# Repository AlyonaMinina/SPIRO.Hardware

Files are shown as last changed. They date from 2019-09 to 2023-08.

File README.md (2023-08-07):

<p align="center">
  SPIRO
</p>
<p align="center">
    <b>S</b>mart <b>P</b>late <b>I</b>maging <b>Ro</b>bot
</p>

[SPIRO](https://www.alyonaminina.org/spiro) is a smart robot for automated time-lapse imaging of biological samples grown on vertically positioned Petri plates: plant seeds, seedlings, bacterial colonies, fungal mycelia, moss etc. The preprint version of our manuscript is available [here](https://www.biorxiv.org/content/10.1101/2021.03.15.435343v1).

SPIRO is controlled by designated software and operated remotely using a web-based user interface [(GitHub repo)](https://github.com/jonasoh/spiro).

We developed two assays to analyze data produced by SPIRO: germination tracking assay optimized for *Arabidopsis thaliana* seeds and root growth tracking assay optimized for *Arabidopsis thaliana* seedlings [(GitHub repo)](https://github.com/jiaxuanleong/spiro-IJmacros).

The SPIRO hardware is constructed from eleven sets of 3D printable structural parts. Sets 3a and 3b are for alternative setups that include either the Arducam motorized focus camera module or the Raspberry Pi v2 camera with manual focus, respectively. Step by step instructions for printing and assembling SPIRO are provided in [the assembly instructions](https://github.com/AlyonaMinina/SPIRO.Hardware/raw/master/1.%20Assembly%20Instructions/SPIRO%20assembly%20instructions.pdf). 

Please refer to **[Table S1](https://github.com/AlyonaMinina/SPIRO.Hardware/raw/master/2.%20Supplementary%20Tables/Table%20S1.%20List%20of%20components%20to%20be%20purchased.pdf)** for the list of components to be purchased and to **[Table S2](https://github.com/AlyonaMinina/SPIRO.Hardware/blob/master/2.%20Supplementary%20Tables/Table%20S2.%20Structural%20parts%20of%20SPIRO%20for%203D%20printing.md)** for instructions on 3D printing. Table S2 also contains several useful accessories for improving the usability of SPIRO.

<p align="center">
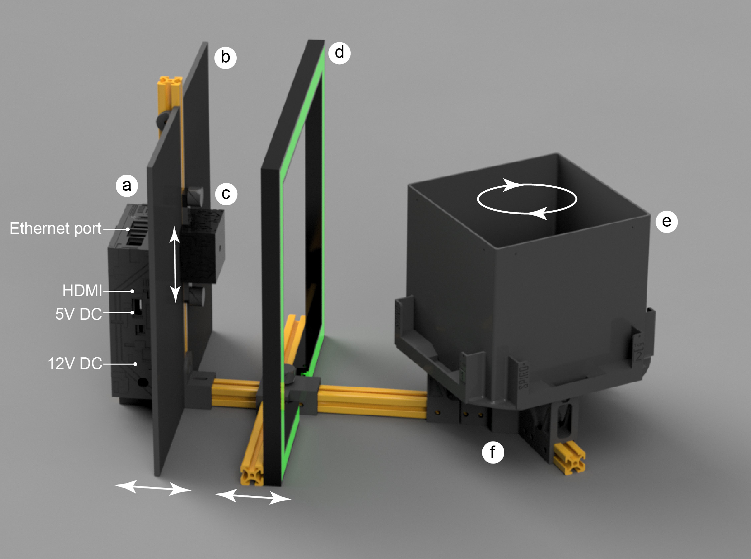
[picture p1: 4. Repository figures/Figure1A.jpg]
SPIRO
  
  SPIRO
</p>

**Figure 1**. SPIRO structure: **a**, Borg's nest harboring the electronics; **b**, vertical rail with the light screen, both can slide along the horizontal rail; **c**, camera house, with adjustable position on the vertical; **d**, LED frame with diffusors, position along the horizontal rail can be adjusted; **e**, rotating stage to hold Petri plates; **f**, motor hub harboring the stepper motor and connecting the horizontal rails. 

<p align="center">
  <br />This work is licensed under a <a rel="license" href="http://creativecommons.org/licenses/by/4.0/">Creative Commons Attribution 4.0 International License</a>.
 </p>

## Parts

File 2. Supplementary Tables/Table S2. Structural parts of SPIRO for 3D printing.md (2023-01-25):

# Table S2. SPIRO components for 3D printing

# Structural parts

| STL file                                                     | Rotation        | Supports    | Brim | Infill | Filament    | Additional info                                              |
| ------------------------------------------------------------ | --------------- | ----------- | ---- | ------ | ----------- | ------------------------------------------------------------ |
| [Set 1](https://github.com/AlyonaMinina/SPIRO.Hardware/raw/master/3.%20Files%20for%20SPIRO%203D%20printable%20hardware/SPIRO%20hardware%20component%20sets/stl%20files/Set%2001.%20Alyona%20Minina.%202019.%20UHEI.stl)| X: 90°          | Build plate | No   | 20%    | Matte black | <details><summary>Set 1. upgraded 2021.05.18 </summary><br/>  [.3mf project file](https://github.com/AlyonaMinina/SPIRO.Hardware/raw/master/3.%20Files%20for%20SPIRO%203D%20printable%20hardware/SPIRO%20hardware%20component%20sets/3mf%20files/Set%2001.%20Alyona%20Minina.%202019.%20UHEI.3mf) <br/>   [.f3d Autodesk Fusion 360 file](https://github.com/AlyonaMinina/SPIRO.Hardware/raw/master/3.%20Files%20for%20SPIRO%203D%20printable%20hardware/SPIRO%20hardware%20component%20sets/Autodesk%20Fusion%20360%20files/Set%2001.%20Alyona%20Minina.%202019.%20UHEI.f3d) <br/> [Preview of layout in Slic3r](https://raw.githubusercontent.com/AlyonaMinina/SPIRO.Hardware/master/3.%20Files%20for%20SPIRO%203D%20printable%20hardware/SPIRO%20hardware%20component%20sets/Screenshots%20of%20slic3r/set%2001.jpg) <br/><br/>**Components list:** <br/>1.	 Motor hub v2 (smoothened corners) <br/>2.	 2x bearing guides<br/>3.	 1x bearing guide with the mount for the mini microswitch v2 (stabilizing the switch)<br/>4. Mini microswitch housing v2  (stabilizing the switch)<br/>5. Mini microswitch pin (tiny dick)<br/>6. Holder for the vertical rail<br/>7. Holder for the LED frame rail<br/>8. 2x bottom for a thumb screw<br/>9. 2x cap for a thumb screw<br/><br/>**Filament use**: 135 g <br/><br/>**Printing time:** 13 h</details> |
| [Set 2](https://github.com/AlyonaMinina/SPIRO.Hardware/raw/master/3.%20Files%20for%20SPIRO%203D%20printable%20hardware/SPIRO%20hardware%20component%20sets/stl%20files/Set%2002.%20Alyona%20Minina.%202019.%20UHEI.stl) | –               | Build plate | No   | 20%    | Matte black | <details><summary>Set 2. upgraded 2021.05.20</summary><br/> [.3mf project file](https://github.com/AlyonaMinina/SPIRO.Hardware/raw/master/3.%20Files%20for%20SPIRO%203D%20printable%20hardware/SPIRO%20hardware%20component%20sets/3mf%20files/Set%2002.%20Alyona%20Minina.%202019.%20UHEI.3mf) <br/> [.f3d Autodesk Fusion 360 file](https://github.com/AlyonaMinina/SPIRO.Hardware/raw/master/3.%20Files%20for%20SPIRO%203D%20printable%20hardware/SPIRO%20hardware%20component%20sets/Autodesk%20Fusion%20360%20files/Set%2002.%20Alyona%20Minina.%202019.%20UHEI.f3d) <br/> [Preview of layout in Slic3r](https://raw.githubusercontent.com/AlyonaMinina/SPIRO.Hardware/master/3.%20Files%20for%20SPIRO%203D%20printable%20hardware/SPIRO%20hardware%20component%20sets/Screenshots%20of%20slic3r/set%2002.jpg)<br/><br/>**Components list:** <br/>1.	Borg's nest (adjusted ethernet port)<br/>2. Lid for the Borg's nest<br/>3. Lid for the DC connector<br/>4. Holder for the SparkFun MOSFET power control kit<br/><br/>**PLA use**: 210 g <br/><br/>**Printing time:** 18.5 h<br/></details> |
| [Set 3a](https://github.com/AlyonaMinina/SPIRO.Hardware/raw/master/3.%20Files%20for%20SPIRO%203D%20printable%20hardware/SPIRO%20hardware%20component%20sets/stl%20files/Set%2003a.%20Alyona%20Minina.%202019.%20UHEI.stl) | X: 90°          | Build plate | No   | 20%    | Matte black | <details><summary>Set 3a</summary><br/>[.3mf project file](https://github.com/AlyonaMinina/SPIRO.Hardware/raw/master/3.%20Files%20for%20SPIRO%203D%20printable%20hardware/SPIRO%20hardware%20component%20sets/3mf%20files/Set%2003a.%20Alyona%20Minina.%202019.%20UHEI.3mf)<br/> [.f3d Autodesk Fusion 360 file](https://github.com/AlyonaMinina/SPIRO.Hardware/raw/master/3.%20Files%20for%20SPIRO%203D%20printable%20hardware/SPIRO%20hardware%20component%20sets/Autodesk%20Fusion%20360%20files/Set%2003a.%20Alyona%20Minina.%202019.%20UHEI.f3d)<br/> [Preview of layout in Slic3r](https://raw.githubusercontent.com/AlyonaMinina/SPIRO.Hardware/master/3.%20Files%20for%20SPIRO%203D%20printable%20hardware/SPIRO%20hardware%20component%20sets/Screenshots%20of%20slic3r/set%2003a.PNG)<br/><br/>**Components list:** <br/>1. Camera housing for Arducam module<br/>2. Lid for the camera housing<br/>3. 2x cap for a thumb screw<br/>4. 2x bottom for a thumb screw<br/>5. washers<br/><br/>**PLA use**: 50 g <br/><br/>**Printing time:** 5 h<br/></details> |
| [Set 3b](https://github.com/AlyonaMinina/SPIRO.Hardware/raw/master/3.%20Files%20for%20SPIRO%203D%20printable%20hardware/SPIRO%20hardware%20component%20sets/stl%20files/Set%2003b.%20Alyona%20Minina.%202019.%20UHEI.stl) | X: 90°          | Build plate | No   | 20%    | Matte black | <details><summary>Set 3b</summary><br/>[.3mf project file](https://github.com/AlyonaMinina/SPIRO.Hardware/raw/master/3.%20Files%20for%20SPIRO%203D%20printable%20hardware/SPIRO%20hardware%20component%20sets/3mf%20files/Set%2003b.%20Alyona%20Minina.%202019.%20UHEI.3mf) <br/> [.f3d Autodesk Fusion 360 file](https://github.com/AlyonaMinina/SPIRO.Hardware/raw/master/3.%20Files%20for%20SPIRO%203D%20printable%20hardware/SPIRO%20hardware%20component%20sets/Autodesk%20Fusion%20360%20files/Set%2003b.%20Alyona%20Minina.%202019.%20UHEI.f3d)<br/> [Preview of layout in Slic3r](https://raw.githubusercontent.com/AlyonaMinina/SPIRO.Hardware/master/3.%20Files%20for%20SPIRO%203D%20printable%20hardware/SPIRO%20hardware%20component%20sets/Screenshots%20of%20slic3r/set%2003b.PNG)<br/><br/>**Components list:** <br/>1. Camera housing for RPi camera<br/>2. Lid for the camera housing<br/>3. 2x bottom for a thumb screw<br/>4. 2x cap for a thumb screw<br/>5. Focusing tool<br/>6. Stabilizer for the camera <br/><br/>**PLA use**: 25 g <br/><br/>**Printing time:** 3 h<br/></details> |
| [Set 4](https://github.com/AlyonaMinina/SPIRO.Hardware/raw/master/3.%20Files%20for%20SPIRO%203D%20printable%20hardware/SPIRO%20hardware%20component%20sets/stl%20files/Set%2004.%20Alyona%20Minina.%202019.%20UHEI.stl) | X: 270°         | Build plate | No   | 20%    | Matte black | <details><summary>Set 4. upgraded 2021.05.20</summary><br/>[.3mf project file](https://github.com/AlyonaMinina/SPIRO.Hardware/raw/master/3.%20Files%20for%20SPIRO%203D%20printable%20hardware/SPIRO%20hardware%20component%20sets/3mf%20files/Set%2004.%20Alyona%20Minina.%202019.%20UHEI.3mf) <br/> [.f3d Autodesk Fusion 360 file](https://github.com/AlyonaMinina/SPIRO.Hardware/raw/master/3.%20Files%20for%20SPIRO%203D%20printable%20hardware/SPIRO%20hardware%20component%20sets/Autodesk%20Fusion%20360%20files/Set%2004.%20Alyona%20Minina.%202019.%20UHEI.f3d) <br/> [Preview of layout in Slic3r](https://raw.githubusercontent.com/AlyonaMinina/SPIRO.Hardware/master/3.%20Files%20for%20SPIRO%203D%20printable%20hardware/SPIRO%20hardware%20component%20sets/Screenshots%20of%20slic3r/set%2004.jpg)<br/><br/>**Components list:** <br/>1. Cube. The rotating stage with holders for Petri plates (adjusted tiny dick orientation) <br/><br/>**PLA use**: 380 g <br/><br/>**Printing time:** 28.5 h<br/></details> |
| [Set 5](https://github.com/AlyonaMinina/SPIRO.Hardware/raw/master/3.%20Files%20for%20SPIRO%203D%20printable%20hardware/SPIRO%20hardware%20component%20sets/stl%20files/Set%2005.%20Alyona%20Minina.%202019.%20UHEI.stl) | Z: 345°  | Everywhere  | Yes  | 50%    | Matte black | <details><summary>Set 5</summary><br/>[.3mf project file](https://github.com/AlyonaMinina/SPIRO.Hardware/raw/master/3.%20Files%20for%20SPIRO%203D%20printable%20hardware/SPIRO%20hardware%20component%20sets/3mf%20files/Set%2005.%20Alyona%20Minina.%202019.%20UHEI.3mf) <br/> [.f3d Autodesk Fusion 360 file](https://github.com/AlyonaMinina/SPIRO.Hardware/raw/master/3.%20Files%20for%20SPIRO%203D%20printable%20hardware/SPIRO%20hardware%20component%20sets/Autodesk%20Fusion%20360%20files/Set%2005.%20Alyona%20Minina.%202019.%20UHEI.f3d) <br/> [Preview of layout in Slic3r](https://raw.githubusercontent.com/AlyonaMinina/SPIRO.Hardware/master/3.%20Files%20for%20SPIRO%203D%20printable%20hardware/SPIRO%20hardware%20component%20sets/Screenshots%20of%20slic3r/set%2005.jpg)<br/><br/>**Components list:** <br/>1. The right half of the light screen<br/><br/>**PLA use**: 260 g <br/><br/>**Printing time:** 23 h<br/><br/>**Notes:** Please ignore messages about toolpath being detected outside the perimeter.</details> |
| [Set 6](https://github.com/AlyonaMinina/SPIRO.Hardware/raw/master/3.%20Files%20for%20SPIRO%203D%20printable%20hardware/SPIRO%20hardware%20component%20sets/stl%20files/Set%2006.%20Alyona%20Minina.%202019.%20UHEI.stl) |  Z: 355° | Everywhere  | Yes  | 50%    | Matte black | <details><summary>Set 6</summary><br/>[.3mf project file](https://github.com/AlyonaMinina/SPIRO.Hardware/raw/master/3.%20Files%20for%20SPIRO%203D%20printable%20hardware/SPIRO%20hardware%20component%20sets/3mf%20files/Set%2006.%20Alyona%20Minina.%202019.%20UHEI.3mf) <br/> [.f3d Autodesk Fusion 360 file](https://github.com/AlyonaMinina/SPIRO.Hardware/raw/master/3.%20Files%20for%20SPIRO%203D%20printable%20hardware/SPIRO%20hardware%20component%20sets/Autodesk%20Fusion%20360%20files/Set%2006.%20Alyona%20Minina.%202019.%20UHEI.f3d)<br/> [Preview of layout in Slic3r](https://raw.githubusercontent.com/AlyonaMinina/SPIRO.Hardware/master/3.%20Files%20for%20SPIRO%203D%20printable%20hardware/SPIRO%20hardware%20component%20sets/Screenshots%20of%20slic3r/set%2006.jpg)<br/><br/>**Components list:** <br/>1. The left half of the light screen<br/><br/>**PLA use**: 230 g <br/><br/>**Printing time:** 20.5 h<br/><br/>**Notes:** Please ignore messages about toolpath being detected outside the perimeter.</details> |
| [Set 7](https://github.com/AlyonaMinina/SPIRO.Hardware/raw/master/3.%20Files%20for%20SPIRO%203D%20printable%20hardware/SPIRO%20hardware%20component%20sets/stl%20files/Set%2007.%20Alyona%20Minina.%202019.%20UHEI.stl) | Z: 50°          | Everywhere  | Yes  | 20%   | Matte black | <details><summary>Set 7</summary><br/>[.3mf project file](https://github.com/AlyonaMinina/SPIRO.Hardware/raw/master/3.%20Files%20for%20SPIRO%203D%20printable%20hardware/SPIRO%20hardware%20component%20sets/3mf%20files/Set%2007.%20Alyona%20Minina.%202019.%20UHEI.3mf) <br/> [.f3d Autodesk Fusion 360 file](https://github.com/AlyonaMinina/SPIRO.Hardware/raw/master/3.%20Files%20for%20SPIRO%203D%20printable%20hardware/SPIRO%20hardware%20component%20sets/Autodesk%20Fusion%20360%20files/Set%2007.%20Alyona%20Minina.%202019.%20UHEI.f3d) <br/> [Preview of layout in Slic3r](https://raw.githubusercontent.com/AlyonaMinina/SPIRO.Hardware/master/3.%20Files%20for%20SPIRO%203D%20printable%20hardware/SPIRO%20hardware%20component%20sets/Screenshots%20of%20slic3r/set%2007.jpg)<br/><br/>**Components list:** <br/>1. The right half of the LED frame<br/><br/>**PLA use**: 140 g <br/><br/>**Printing time:** 14 h<br/><br/>**Notes:** Please ignore messages about toolpath being detected outside the perimeter.</details> |
| [Set 8](https://github.com/AlyonaMinina/SPIRO.Hardware/raw/master/3.%20Files%20for%20SPIRO%203D%20printable%20hardware/SPIRO%20hardware%20component%20sets/stl%20files/Set%2008.%20Alyona%20Minina.%202019.%20UHEI.stl) | Z: 50°          | Everywhere  | Yes  | 20%    | Matte black | <details><summary>Set 8</summary><br/>[.3mf project file](https://github.com/AlyonaMinina/SPIRO.Hardware/raw/master/3.%20Files%20for%20SPIRO%203D%20printable%20hardware/SPIRO%20hardware%20component%20sets/3mf%20files/Set%2008.%20Alyona%20Minina.%202019.%20UHEI.3mf) <br/> [.f3d Autodesk Fusion 360 file](https://github.com/AlyonaMinina/SPIRO.Hardware/raw/master/3.%20Files%20for%20SPIRO%203D%20printable%20hardware/SPIRO%20hardware%20component%20sets/Autodesk%20Fusion%20360%20files/Set%2008.%20Alyona%20Minina.%202019.%20UHEI.f3d)<br/> [Preview of layout in Slic3r](https://raw.githubusercontent.com/AlyonaMinina/SPIRO.Hardware/master/3.%20Files%20for%20SPIRO%203D%20printable%20hardware/SPIRO%20hardware%20component%20sets/Screenshots%20of%20slic3r/set%2008.jpg)<br/><br/>**Components list:** <br/>1. The left half of the LED frame<br/><br/>**PLA use**: 130 g <br/><br/>**Printing time:** 12.5 h<br/><br/>**Notes:** Please ignore messages about toolpath being detected outside the perimeter.</details> |
| [Set 9](https://github.com/AlyonaMinina/SPIRO.Hardware/raw/master/3.%20Files%20for%20SPIRO%203D%20printable%20hardware/SPIRO%20hardware%20component%20sets/stl%20files/Set%2009.%20Alyona%20Minina.%202019.%20UHEI.stl) | Z: 50°          | –           | Yes  | 30%    | Transparent | <details><summary>Set 9</summary><br/>[.3mf project file](https://github.com/AlyonaMinina/SPIRO.Hardware/raw/master/3.%20Files%20for%20SPIRO%203D%20printable%20hardware/SPIRO%20hardware%20component%20sets/3mf%20files/Set%2009.%20Alyona%20Minina.%202019.%20UHEI.3mf) <br/> [.f3d Autodesk Fusion 360 file](https://github.com/AlyonaMinina/SPIRO.Hardware/raw/master/3.%20Files%20for%20SPIRO%203D%20printable%20hardware/SPIRO%20hardware%20component%20sets/Autodesk%20Fusion%20360%20files/Set%2009.%20Alyona%20Minina.%202019.%20UHEI.f3d) <br/> [Preview of layout in Slic3r](https://raw.githubusercontent.com/AlyonaMinina/SPIRO.Hardware/master/3.%20Files%20for%20SPIRO%203D%20printable%20hardware/SPIRO%20hardware%20component%20sets/Screenshots%20of%20slic3r/set%2009.jpg) <br/><br/>**Components list:** <br/>1. Left diffuser<br/>2. Bottom left diffuser<br/>3. Bottom right diffuser<br/><br/>**PLA use**: 35 g <br/><br/>**Printing time:** 2.5 h<br/></details> |
| [Set 10](https://github.com/AlyonaMinina/SPIRO.Hardware/raw/master/3.%20Files%20for%20SPIRO%203D%20printable%20hardware/SPIRO%20hardware%20component%20sets/stl%20files/Set%2010.%20Alyona%20Minina.%202019.%20UHEI.stl) | Z: 40°          | –           | Yes  | 30%    | Transparent | <details><summary>Set 10</summary><br/>[.3mf project file](https://github.com/AlyonaMinina/SPIRO.Hardware/raw/master/3.%20Files%20for%20SPIRO%203D%20printable%20hardware/SPIRO%20hardware%20component%20sets/3mf%20files/Set%2010.%20Alyona%20Minina.%202019.%20UHEI.3mf)<br/> [.f3d Autodesk Fusion 360 file](https://github.com/AlyonaMinina/SPIRO.Hardware/raw/master/3.%20Files%20for%20SPIRO%203D%20printable%20hardware/SPIRO%20hardware%20component%20sets/Autodesk%20Fusion%20360%20files/Set%2010.%20Alyona%20Minina.%202019.%20UHEI.f3d)<br/> [Preview of layout in Slic3r](https://raw.githubusercontent.com/AlyonaMinina/SPIRO.Hardware/master/3.%20Files%20for%20SPIRO%203D%20printable%20hardware/SPIRO%20hardware%20component%20sets/Screenshots%20of%20slic3r/set%2010.jpg)<br/><br/>**Components list:** <br/>1. Top diffuser<br/><br/>**PLA use**: 20 g <br/><br/>**Printing time:** 1.5 h<br/></details> |
| [Set 11](https://github.com/AlyonaMinina/SPIRO.Hardware/raw/master/3.%20Files%20for%20SPIRO%203D%20printable%20hardware/SPIRO%20hardware%20component%20sets/stl%20files/Set%2011.%20Alyona%20Minina.%202019.%20UHEI.stl) | Z: 50°          | –           | Yes  | 30%    | Transparent | <details><summary>Set 11</summary><br/>[.3mf project file](https://github.com/AlyonaMinina/SPIRO.Hardware/raw/master/3.%20Files%20for%20SPIRO%203D%20printable%20hardware/SPIRO%20hardware%20component%20sets/3mf%20files/Set%2011.%20Alyona%20Minina.%202019.%20UHEI.3mf) <br/> [.f3d Autodesk Fusion 360 file](https://github.com/AlyonaMinina/SPIRO.Hardware/raw/master/3.%20Files%20for%20SPIRO%203D%20printable%20hardware/SPIRO%20hardware%20component%20sets/Autodesk%20Fusion%20360%20files/Set%2011.%20Alyona%20Minina.%202019.%20UHEI.f3d)<br/> [Preview of layout in Slic3r](https://raw.githubusercontent.com/AlyonaMinina/SPIRO.Hardware/master/3.%20Files%20for%20SPIRO%203D%20printable%20hardware/SPIRO%20hardware%20component%20sets/Screenshots%20of%20slic3r/set%2011.jpg) <br/><br/>**Components list:** <br/>1. Right diffuser<br/><br/>**PLA use**: 20 g <br/><br/>**Printing time:** 1.4 h<br/></details> |

## Notes
As of today, printing structural parts has been tested using PLA filaments only.
Required total amount of black matt PLA = 1685 g <br>Required total amount of milky white PLA = 75 g<br>Total estimated time of printing = 159.5 h

# Accessories

| STL file                                                     | Rotation        | Supports    | Brim | Infill | Filament    | Additional info                                              |
| ------------------------------------------------------------ | --------------- | ----------- | ---- | ------ | ----------- | ------------------------------------------------------------ |
| [Anti-reflection lids for square 12 cm plates](https://github.com/AlyonaMinina/SPIRO.Hardware/raw/master/3.%20Files%20for%20SPIRO%203D%20printable%20hardware/SPIRO%20accessories/stl%20files/anti-reflection%20lid%20for%2012%20cm%20square%20Petri%20plates%20v5.stl)| Y: 180°          | - | No   | 20%    | PETG black and white | <details><summary>Important!</summary><br/>[.3mf project file](https://github.com/AlyonaMinina/SPIRO.Hardware/raw/master/3.%20Files%20for%20SPIRO%203D%20printable%20hardware/SPIRO%20accessories/3mf%20files/anti-reflection%20lid%20for%2012%20cm%20square%20Petri%20plates%20v5.3mf) <br/> [Preview of layout in Slic3r](https://raw.githubusercontent.com/AlyonaMinina/SPIRO.Hardware/master/3.%20Files%20for%20SPIRO%203D%20printable%20hardware/SPIRO%20accessories/Screenshots%20of%20slic3r/anti-reflection%20lid%20for%2012%20cm%20square%20Petri%20plates%20v5.png)<br/><br/>**Printing instructions:** For the sake of durability, we strongly recommend using PETG plastic.<br/>[The lid should be printed in two colors](https://www.alyonaminina.org/anti-relflection-lids): the inner pane of the lid should be black and ironed to provide evenly contrasting background for seeds and seedlings, while the rims of the lid should be white to reduce shading and reflect the light back into the plate. <br/>Ironing during printing might result in an unwanted shiny finish of the surface, this can be avoided by manually lowering down the nozzle temperature during printing the ironed level. In our experience, using 190–200 C nozzle temperature results in a matte finish while using PETG filament.<br/>The .3mf file contains information required for printing using a Prusa i3 MK3/S printer and can be modified for any other printer.<br/><br/><br/>**Filament use**: 41 g <br/>**Printing time:** 6 h</details> |
| [Anti-reflection lids for round 9 cm plates](https://github.com/AlyonaMinina/SPIRO.Hardware/raw/master/3.%20Files%20for%20SPIRO%203D%20printable%20hardware/SPIRO%20accessories/stl%20files/anti-reflection%20lid%20for%209%20cm%20round%20Petri%20plates%20v3.stl)| Y: 180°          | - | No   | 20%    | PETG black and white| <details><summary>Important!</summary><br/>[.3mf project file](https://github.com/AlyonaMinina/SPIRO.Hardware/raw/master/3.%20Files%20for%20SPIRO%203D%20printable%20hardware/SPIRO%20accessories/3mf%20files/anti-reflection%20lid%20for%209%20cm%20round%20Petri%20plates%20v5.3mf) <br/> [Preview of layout in Slic3r](https://raw.githubusercontent.com/AlyonaMinina/SPIRO.Hardware/master/3.%20Files%20for%20SPIRO%203D%20printable%20hardware/SPIRO%20accessories/Screenshots%20of%20slic3r/anti-reflection%20lid%20for%209%20cm%20round%20Petri%20plates%20v5.png) <br/><br/>**Printing instructions:** For the sake of durability, we strongly recommend using PETG plastic.<br/>[The lid should be printed in two colors](https://www.alyonaminina.org/anti-relflection-lids): the inner pane of the lid should be black and ironed to provide evenly contrasting background for seeds and seedlings, while the rims of the lid should be white to reduce shading and reflect the light back into the plate.<br/>Ironing during printing might result in an unwanted shiny finish of the surface, this can be avoided by manually lowering down the nozzle temperature during printing the ironed level. In our experience, using 190–200 C nozzle temperature results in a matte finish while using PETG filament.<br/>.3mf file contains information required for printing using a Prusa  i3 MK3/S printer and can be modified for any other printer. <br/><br/><br/>**Filament use**: 18 g <br/>**Printing time:** 3.5 h</details> |
| [Seed plating guide for square 12 cm plates](https://github.com/AlyonaMinina/SPIRO.Hardware/raw/master/3.%20Files%20for%20SPIRO%203D%20printable%20hardware/SPIRO%20accessories/stl%20files/SPIRO%20seed%20plating%20guide%20for%2012cm%20square%20plates.stl)|-         | - | No  | 15%    | Any | <details><summary>More info</summary><br/>[.3mf project file]() <br/> [Preview of layout in Slic3r](https://raw.githubusercontent.com/AlyonaMinina/SPIRO.Hardware/master/3.%20Files%20for%20SPIRO%203D%20printable%20hardware/SPIRO%20accessories/Screenshots%20of%20slic3r/SPIRO%20seed%20plating%20guide%20for%2012%20cm%20square%20plates.png) <br/><br/>**Components list:**<br/>1. Seed plating guide for square 12 cm plates<br/>**Filament use**: 59 g <br/><br/>**Printing time:** 14.5 h</details> |
| [Seed plating guide for round 9 cm plates](https://github.com/AlyonaMinina/SPIRO.Hardware/raw/master/3.%20Files%20for%20SPIRO%203D%20printable%20hardware/SPIRO%20accessories/stl%20files/SPIRO%20seed%20plating%20guide%20for%209%20cm%20round%20plates.stl)| Y: 270°          | - | No   | 15%    | Any | <details><summary>More info</summary><br/>[.3mf project file](https://github.com/AlyonaMinina/SPIRO.Hardware/raw/master/3.%20Files%20for%20SPIRO%203D%20printable%20hardware/SPIRO%20accessories/3mf%20files/SPIRO%20seed%20plating%20guide%20for%209%20cm%20round%20plates.3mf) <br/> [Preview of layout in Slic3r](https://raw.githubusercontent.com/AlyonaMinina/SPIRO.Hardware/master/3.%20Files%20for%20SPIRO%203D%20printable%20hardware/SPIRO%20accessories/Screenshots%20of%20slic3r/SPIRO%20seed%20plating%20guide%20for%209%20cm%20round%20plates.png)<br/><br/>**Components list:**<br/>1. Seed plating guide for round 9 cm plates<br/>**Filament use**: 51 g <br/><br/>**Printing time:** 9.5 h</details> |
| [Seed plating guides and insets for multi-well Petri plates](https://www.thingiverse.com/thing:4196441)| -        | - | No   | -    | PETG, white | <details><summary>More info</summary><br/>[Slic3r image](https://github.com/AlyonaMinina/SPIRO.Hardware/blob/35078685dc392920a96c7bca84eb9606d9b28ead/3.%20SPIRO%20hardware.%20stl%20files%20for%20printable%20sets/Screenshots%20of%20slic3r/set%2001.jpg) <br/><br/>[For more information please refer to Thingiverse](https://www.thingiverse.com/thing:4196441)<br/> |

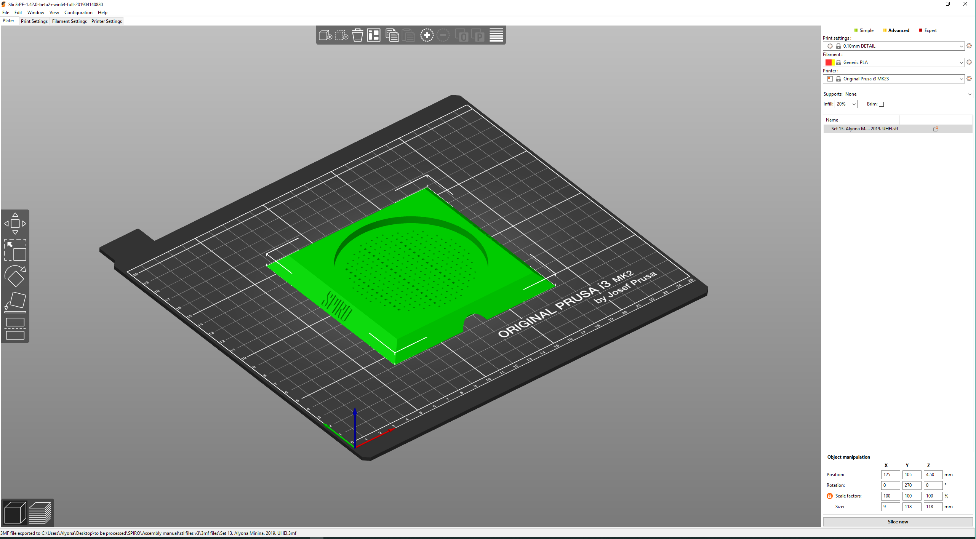
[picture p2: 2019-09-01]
3. Files for SPIRO 3D printable hardware/SPIRO hardware component sets/Screenshots of slic3r/set 13.PNG

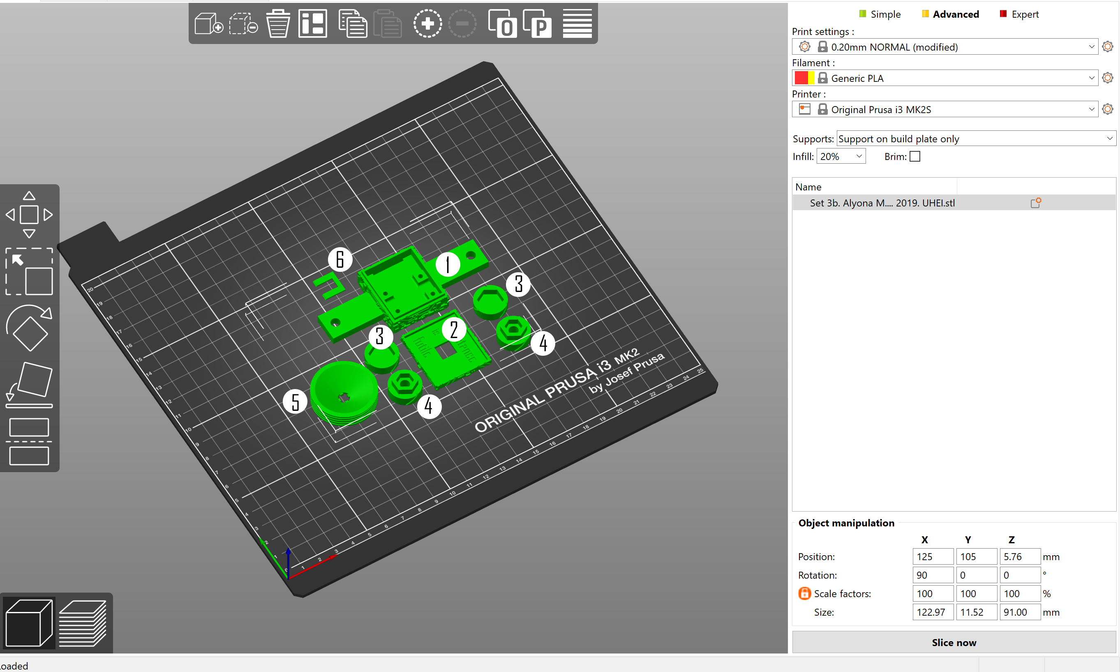
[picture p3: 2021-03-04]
3. Files for SPIRO 3D printable hardware/SPIRO hardware component sets/Screenshots of slic3r/set 03b.PNG

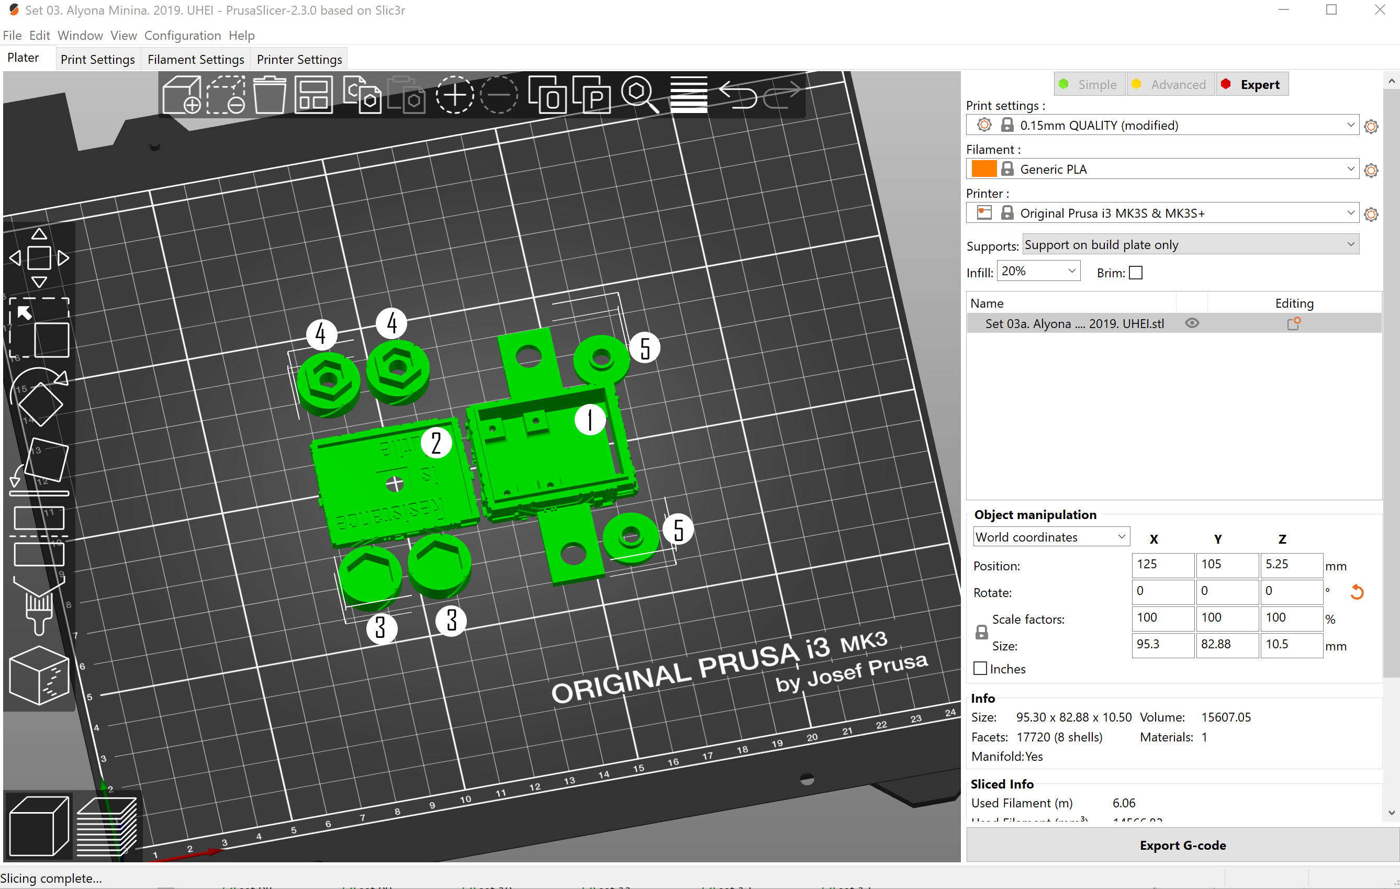
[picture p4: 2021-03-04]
3. Files for SPIRO 3D printable hardware/SPIRO hardware component sets/Screenshots of slic3r/set 03a.PNG

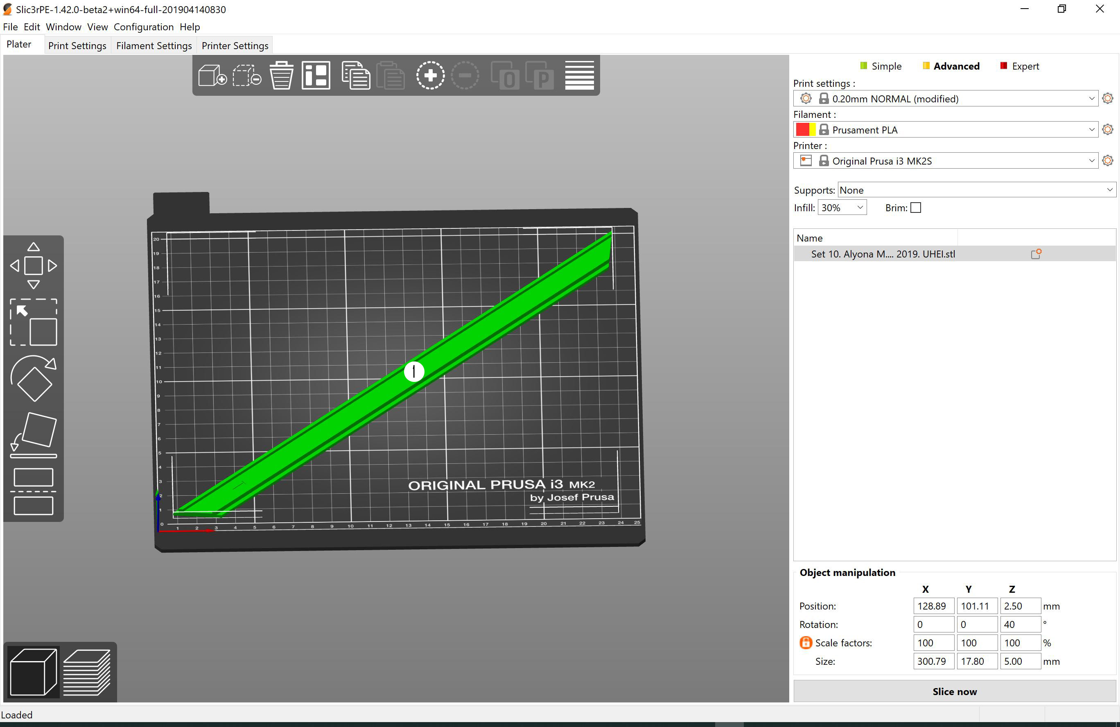
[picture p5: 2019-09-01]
3. Files for SPIRO 3D printable hardware/SPIRO hardware component sets/Screenshots of slic3r/set 10.jpg

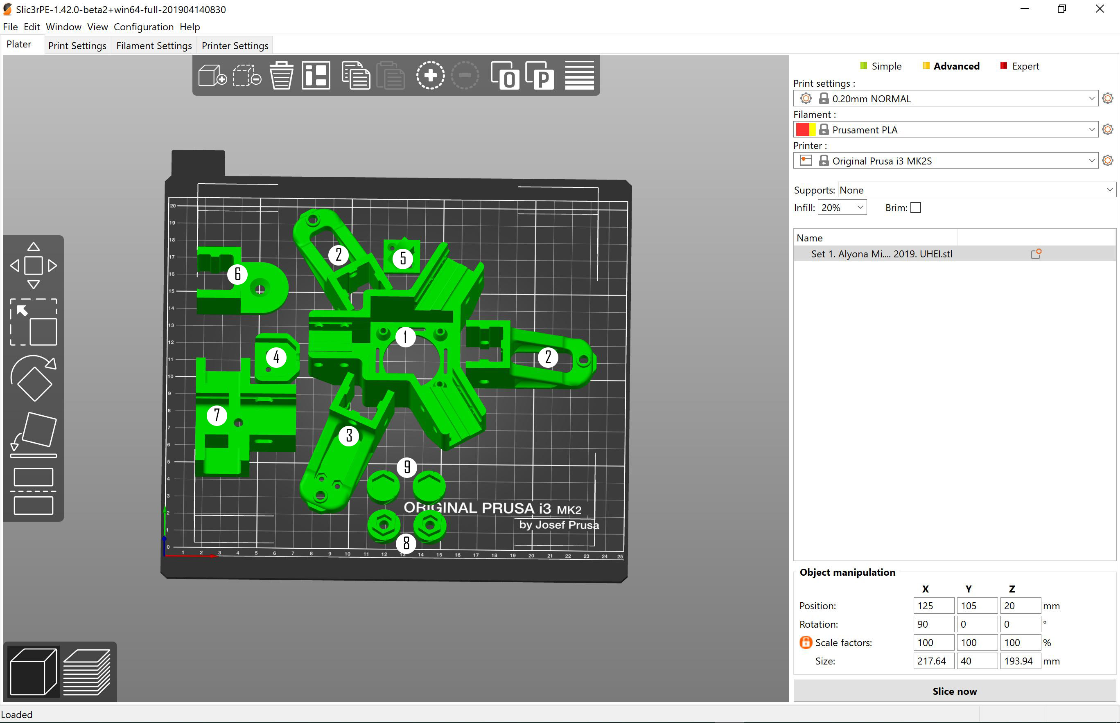
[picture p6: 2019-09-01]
3. Files for SPIRO 3D printable hardware/SPIRO hardware component sets/Screenshots of slic3r/set 01.jpg

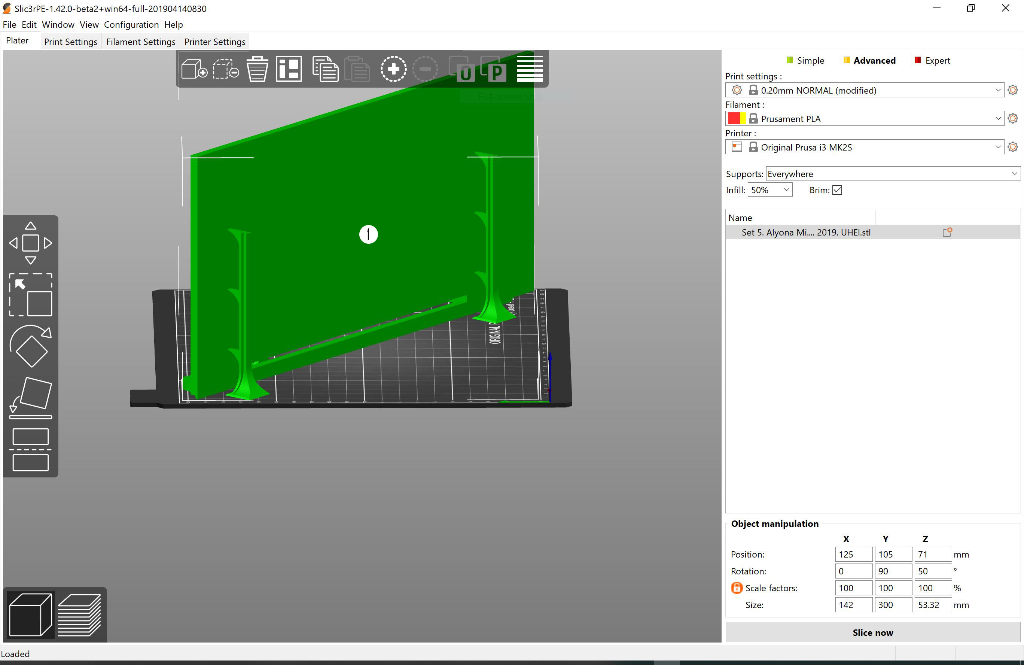
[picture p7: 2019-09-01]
3. Files for SPIRO 3D printable hardware/SPIRO hardware component sets/Screenshots of slic3r/set 05.jpg

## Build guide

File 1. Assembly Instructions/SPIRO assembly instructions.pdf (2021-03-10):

# SPIRO

# Assembly instructions

SPIRO assembly instructions v6

1

### Contents

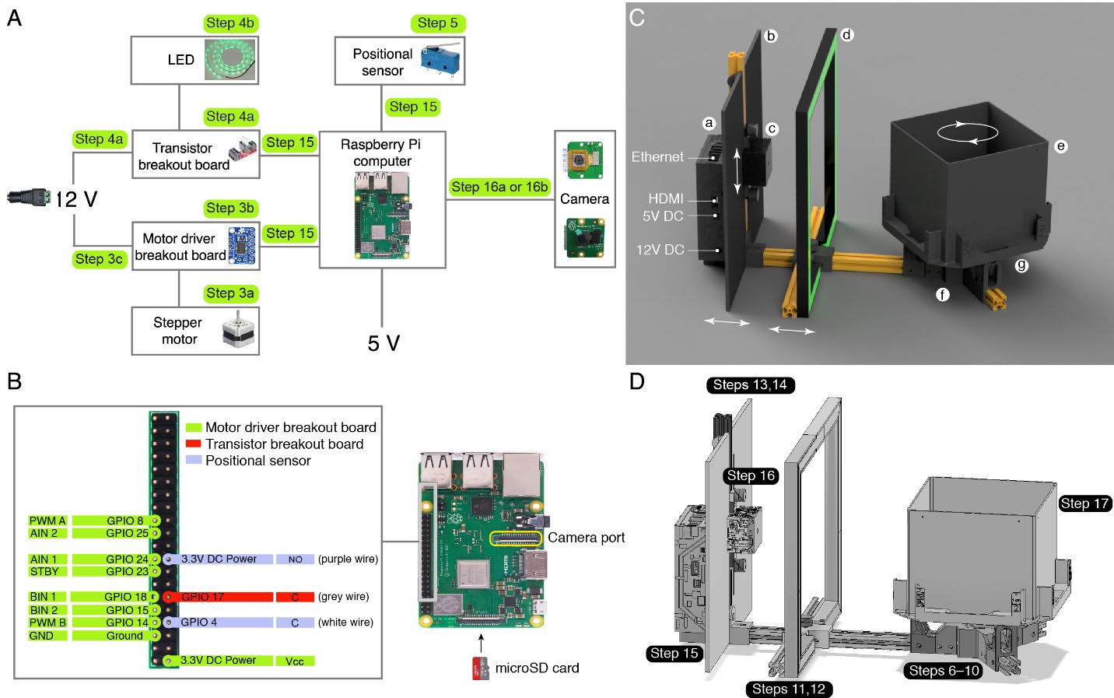
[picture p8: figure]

2

### Overview

SPIRO, the Smart Plate Imaging Robot, is a simple imaging system that comprises only a handful of electronics components (Fig. 1A-B) and has 3D-printable structural parts (Fig. 1C-D). It is designed for automated time-lapse imaging of samples growing on vertically positioned Petri plates, e.g., plant seeds and seedlings, calli, bacterial colonies, fungi, and moss.

Figure 1. SPIRO electronics components.
(A) SPIRO wiring scheme. The system can be equipped with either an Arducam camera module with motorized focus mounted on the Raspberry Pi v2 camera (step 16a) or a Raspberry Pi camera with manual focus (step 16b). (B) Pinout schematic. The camera is powered and controlled via the camera port on the Raspberry Pi board (yellow frame). (C) Overview of SPIRO structural parts: a, Borg's nest harboring the electronics; b, vertical rail with light screen (position can be adjusted along the horizontal rail); c, camera house (position vertically adjustable); d, LED frame with diffusors (horizontally adjustable); e, rotating stage to hold Petri plates; f, motor hub harboring stepper motor and connecting the horizontal rails; g, positional sensor (mini microswitch) used to align the position of the rotating stage with the camera. (D) Overview of steps to assemble the structural parts.
A single Raspberry Pi computer controls the rest of SPIRO’s electronic components: camera, positional sensor, stepper motor and LEDs. Here we describe two possible configurations of SPIRO with or without motorized focus for the camera. SPIRO is controlled

3

remotely via a web-based user interface, and the motorized camera module allows convenient focus adjustment from the software. However, this configuration is about 25 euros more expensive. A positional microswitch ensures that the Petri plates will be placed straight in front of the camera during imaging. LEDs are powered by a 12 V power supply unit, and switched on/off via a transistor. The stepper motor rotating the stage is controlled via the motor driver breakout board and powered by the same 12 V power supply unit. The SPIRO program and underlying operating system are installed on a microSD card.
SPIRO’s laconic configuration was fine-tuned for assembly without any previous experience in 3D printing, use of Raspberry Pi, and mechanical engineering. The user will need to acquire basic knowledge of soldering, which was verified to be achievable by watching a tutorial YouTube video¹. (https://www.youtube.com/watch?v=Qps9woUGkvI&ab_channel=oneTesla)
SPIRO is assembled in 17 main steps, as described below. The time required for assembly (starting from the step 3) can range from several hours to several days depending on the user’s skills in wielding a screwdriver. The time required for printing the structural parts is typically seven days, although it can be shorter when using more than one printer.

4

We strongly recommend to check for potential updates in the SPIRO Hardware Repository² prior to purchasing or printing components.

### 1. Purchase components from Table S1

SPIRO includes a number of standard structural and electronic components that need to be purchased. The complete list of components, required amounts and suggestions for distributors can be found in Table S1 of the manuscript and in the SPIRO Hardware Repository².

Please note that shipment costs comprise about a quarter of the building price for a single SPIRO. Additionally, some of the components can be ordered only in superfluous amounts, e.g., LED strip. Thus, building several SPIROs simultaneously will likely reduce the cost per robot.

### 2. Print structural parts of SPIRO

The printable structural parts of SPIRO are combined into 11 sets (Table S2, File S1, SPIRO Hardware Repository²). According to our experience, printing all sets takes approximately seven days and requires about 1.5 kg of matte black PLA plastic and 100 g of semi-transparent PLA plastic.

All components were printed using Prusa i3 MK2S printer and additionally tested on a Prusa i3 MK3. If you do not have access to a 3D printer, it is possible to find publicly available printers in centers like Makerspaces (https://www.makerspaces.com/what-is-a-makerspace/) or, alternatively, to order 3D prints from online services (3dhubs (https://downloads.3dhubs.com/3D_Hubs_Capabilities.pdf) or similar).

We have thoroughly verified and optimized printing settings for each set of parts. It is highly recommended to follow the printing instructions provided in the table to achieve the best possible quality. As of today, SPIRO hardware has been tested using only PLA plastic. It is sufficiently robust, is the cheapest type of filament and also the easiest one to print with. If desired, SPIRO can be also printed using PETG or ABS filament, however it might require adjustments in scaling of the models to compensate for shrinkage of the printed parts.

For 3D printing, model files need to be converted into g-code files, which then can be read by a 3D printer to print the component. Such conversion can be done in a slicing

5

software of users’ choice. For this project we used PrusaSlicer v2.1³. In addition to the physical parameters of a printable object, g-code files also contain information about the type of filament and the printer to be used, how much plastic should be used for filling in the object’s volume (infill), position of the model on the print bed etc.

File S1 contains .stl, .3mf and .f3d type of files for each hardware set of SPIRO. Additionally, we include screenshots of creating g-code files for each SPIRO set in PrusaSlicer.

.stl files can be used to create g-code files in any slicing software. Please use the printing settings recommended in Table S2 of the manuscript or the SPIRO Hardware Repository².

.3mf project files already contain recommended settings optimized for printing using Prusa i3 MK3/S. These files can be used for example in the PrusaSlicer software to adjust filament and printer settings and generate g-codes files.

.f3d can be used for modifying our design. This can be done using the Autodesk Fusion 360 software, which is distributed with free license for educational facilities.

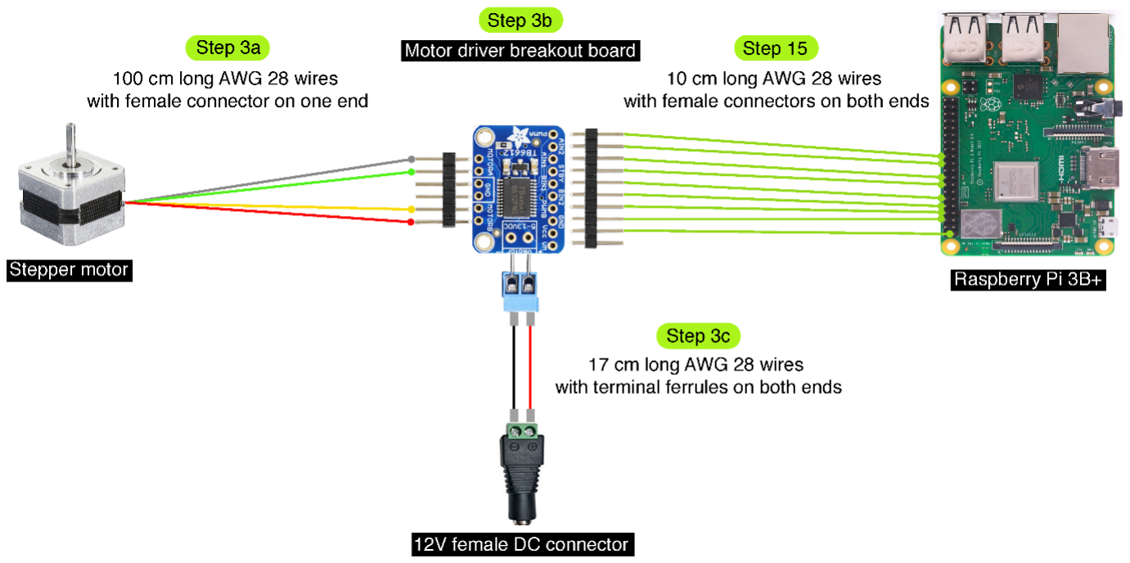
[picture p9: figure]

6

### 3. Wire the stepper motor

Figure 2. Wiring the stepper motor.
This step comprises three sub-steps: 3a, soldering four wires to the motor to have a total length of 100 cm and adding female connectors. 3b, soldering components to the motor driver breakout board (see Fig. 3): the pin headers (b) and the two-pin screw terminal (c) should be soldered to the board (a). Note the orientation of the parts in the description in the corresponding section. 3c, wiring the 12 V DC female connector to the screw terminal on the motor driver breakout board. Connecting the wires from the motor to the driver and from the driver to the Raspberry Pi is done in a later (step 15).

7

3a. Solder stepper motor wires

Each of the four wires of the motor should be extended to a total length of 100 cm and have a female connector at the end.

- The type of solder wire we have used contains 60% tin and 40% lead with a rosin core. However, due to health reasons it is generally recommended to use lead free solder wire.
- When extending the wires, please use jumper cables with colors corresponding to the wires already attached to the motor: grey, green, yellow, red (Fig. 2).
- Total length of each wire: wire already connected to the stepper motor + AWG 28 cable + jumper cable with one female connector = 100 cm.
- Measure the length of the wires already attached to the motor.
- Cut off one connector from the jumper cable to leave only one female connector attached.
- Cut the AWG 28 cables to the length required so that each wire is 100 cm in total length.
- Follow the instructions in video 3a. Stepper motor wires (https://youtu.be/ByPWDRsGsjY) for wire connection and insulation.
Component | # in Table S1
NEMA 17 stepper motor | 4
AWG 28 color cables | 15
AWG 28 jumper cables with female connector | 11
Heat-shrink tube 1–2mm in diameter | 13
Tool | # in Table S1
Soldering iron + solder | 46
Lighter | –
Scissors | –
Wire stripper | 44

8

3b. Solder the motor driver breakout board

- Solder the pin headers to the board with the long pins extending from the labeled side of the board (Fig. 3A). The pin headers are included into the Motor driver breakout board kit as a single strip that needs to be broken into two shorter strips with 6 and 10 pins.
- Solder the two-pin screw terminal to the Vmotor holes. Make sure that the terminal and the long pins are on the same side of the board and that the metal ports of the terminal are facing away from the board (Fig. 3B).

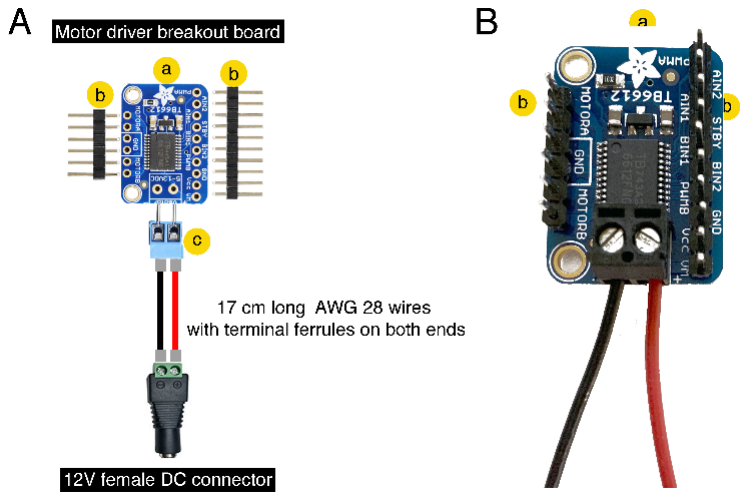
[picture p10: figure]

Figure 3. Soldering the motor driver breakout board components.
(A) Components to be soldered: a, PCB; b, pin headers; c, two-pin screw terminal.
(B) Soldered driver with power wires connected to the screw terminal.
Component | # in Table S1
Motor driver breakout board kit | 3
Two-pin screw terminal 3.5 mm pitch | 10 (if not included in the kit)
Tool | # in Table S1
Soldering iron + solder | 46

9

3c. Wire the motor driver to the DC connector

- Use two 17 cm long AWG 28 wires (black and red).
- Secure terminal ferrules on both ends of each wire. For instructions see the video Securing terminal ferrules. (https://youtu.be/44h8z8VTbQU)
- Connect the “+“ screw port of the motor driver and the DC connector using the red wire, and the “–“ port with the black wire.
- Tighten the screws to secure the wires in place.
- Please note that there will be another pair of wires going into the ports of the DC connector to power the SparkFun MOSFET power control kit (Fig. 5D).
Component | # in Table S1
AWG 28 color cables | 15
Terminal ferrules 0.5 mm² (not insulated) | 14
Heat-shrink tube 2 mm in diameter | 13
Tool | # in Table S1
Lighter | –
Scissors | –
Wire stripper | 44
Ferrule crimper | 45

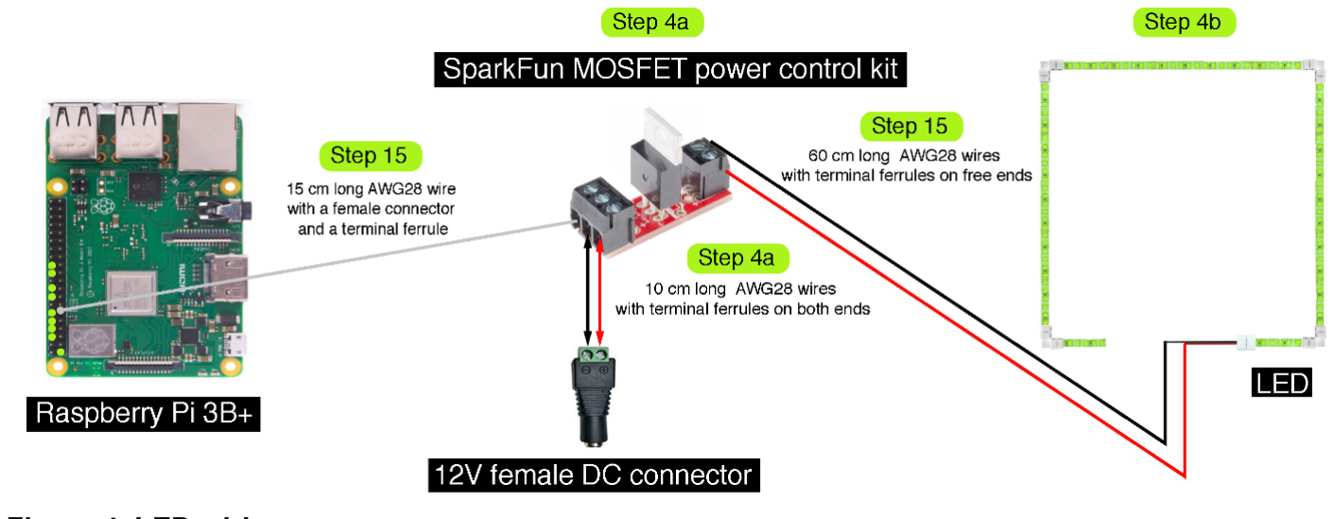
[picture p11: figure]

10

### 4. LED wiring

Figure 4. LED wiring.
These steps will include soldering the transistor that will be used to control the LED (SparkFun MOSFET power control kit, step 4a) and connecting the transistor to the 12V DC power supply. The LED strip is assembled into a square using 90° corner connectors (step 4b) and a terminal LED connector. The LED is attached to the SparkFun MOSFET power control kit later during SPIRO assembly (step 15).

11

4a. Assemble the SparkFun MOSFET power control kit

- Solder the resistor, transistor and both screw terminals to the SparkFun MOSFET power control kit board (Fig. 5).

Important! Don’t be like Jonas, take extra care to solder part b in the correct direction (Fig. 5B and C).

- Trim the ends of b and c after the soldering is complete (Fig. 5).
- Connect the three-pin screw terminal to the 12V DC connector:
- Use two 10 cm long 28 AWG wires (black and red).
- Secure electric wire ferrules on both ends of each wire. For instructions see the video Securing terminal ferrules. (https://youtu.be/44h8z8VTbQU)
- Use the red wire to connect the “+“ port of the three-pin screw terminal of the SparkFun kit to the “+” port of the DC connector.
- Use the black wire to connect the “–“ port of the three-pin screw terminal of the SparkFun kit to the “–” port of the DC connector.
- Tighten the screws to secure wires in place.
- Use a 15 cm long grey jumper cable with a female connector. Secure an electric wire ferrule on the free end of the wire. For instructions, see the video Securing terminal ferrules. (https://youtu.be/44h8z8VTbQU)
- Place the ferrule protected end of this wire into the “C” port of the three-pin screw terminal.

Figure 5. Assembling
the SparkFun MOSFET
power control kit
(A) Components to be
soldered: a, PCB; b, transistor; c, resistor, d,
three-pin screw terminal;
e, two-pin screw terminal
(the photo is modified

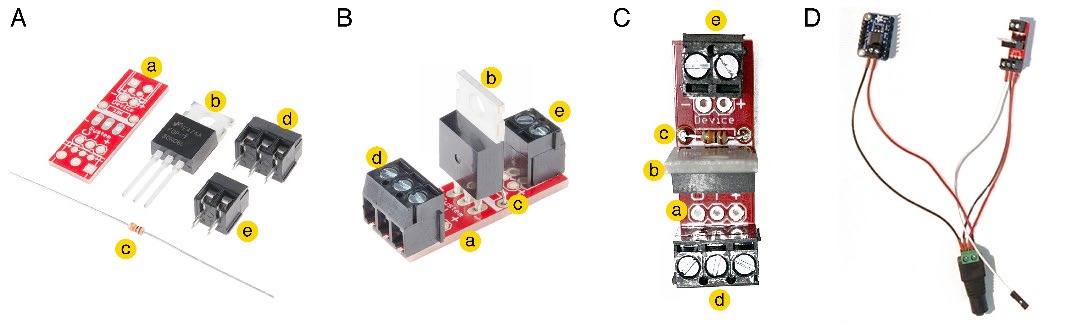
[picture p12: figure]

from SparkFun.com). (B) The side view of the soldered kit. Please note the orientation of the transistor (b) and the screw terminals (d and e). (C) Top view of the soldered kit, note the orientation of the transistor (b) and position of the resistor (c). (D) SparkFun MOSFET power control kit and motor driver wired to the 12V female DC connector.

Component | # in Table S1

12

SparkFun MOSFET power control kit | 7
AWG 28 color cables | 15
Terminal ferrules 0,5 mm² (not insulated) | 14
Heat-shrink tube 2mm in diameter | 13
Tool | # in Table S1
Soldering iron + solder | 46
Lighter | –
Scissors | –
Wire stripper | 44
Ferrule crimper | 45

13

4b. Solder wires to the LED terminal connector and assemble the LED strip

- Cut the LED strip into three 25 cm long segments (these will be the left, top and right parts of the LED square) and two 5 cm long segments (these will be the bottom left and bottom right parts of the LED square). Connect the segments using the corner connectors. Make sure the “+” contacts on the corners are connected to the “+” contacts on the LED strip (Fig. 4).
- Extend the two wires already attached to the LED terminal connectors so that they have a total length of 50 cm.
- Crimp a ferrule onto the free end of each wire and secure it with the heat-shrink tube. For instructions, see the video Securing terminal ferrules. (https://youtu.be/44h8z8VTbQU)
- Bind both wires together with a coiled cable protection. Cover the 40 cm length starting from the connector. Leave the last 10 cm free of cover.
- Attach the terminal connector to the right bottom strip of the LED square. For instructions, see the video LED strip assembly. (https://youtu.be/kxTCNyMMx3A)
Component | # in Table S1
8 mm green LED strip | 8
4x 8 mm 2-pin LED strip corner connectors | 9
8 mm 2-pin LED strip terminal connector | 9
AWG 28 color cables | 15
Terminal ferrules 0,5 mm² (not insulated) | 14
Heat-shrink tube 2mm in diameter | 13
Coiled cable protection | 16
Tool | # in Table S1
Soldering iron + solder | 46
Lighter | –
Scissors | –
Wire stripper | 44
Ferrule crimper | 45

14

### 5. Solder the positional sensor (mini microswitch) wires

- Solder two 110 cm long AWG 28 wires to the microswitch contacts (Fig. 6):
- The purple wire should be attached to contact “NO”.
- The white wire should be attached to contact “C”.
- Each wire should end with a female connector.
- Follow the instructions in video 3a. Stepper motor wires (https://youtu.be/ByPWDRsGsjY) for wire connection and insulation.
Component | # in Table S1
Positional sensor (mini microswitch) | 19
AWG 28 color cables | 15
AWG 28 jumper cables with a female connector | 11
Heat-shrink tube 2 mm in diameter | 13
Tool | # in Table S1
Soldering iron + solder | 46
Lighter | –
Scissors | –
Wire stripper | 44
Figure 6. Wiring the positional microswitch.
| The positional microswitch acts as a bridge be- tween the 3.3V pin on the Raspberry Pi (purple wire) and its GPIO pin (white wire). When the switch is activated, the bridge is closed, indi- cating the position of the imaging stage.

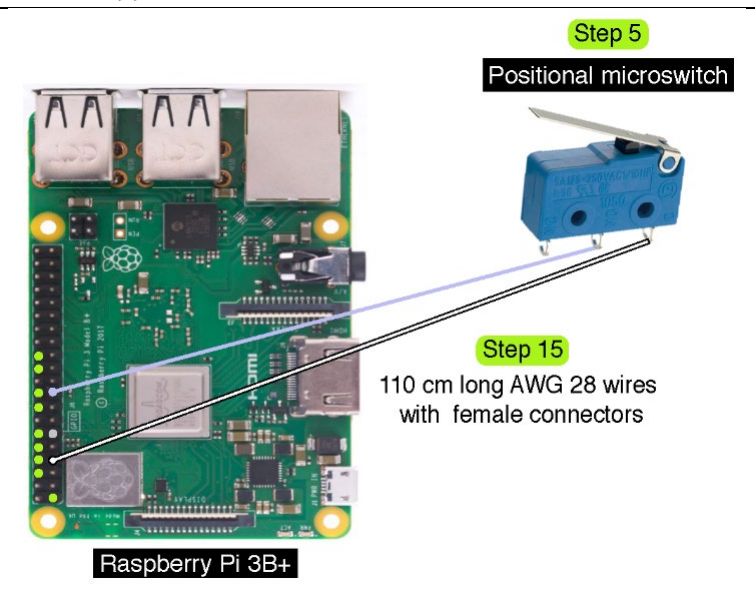
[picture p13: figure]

15

### 6. Mount the motor hub

Follow instructions in video 6. Mounting the motor hub. (https://youtu.be/KKyhD00CaCU)

Component | # in Table S1
The stepper motor wired in the step 3 | -
4x M3 screws, 12 mm long | 28
Component | # in Table S2 (https://github.com/AlyonaMinina/SPIRO.Hardware/blob/master/Supplementary%20Tables/Table%20S2.%20Structural%20parts%20of%20SPIRO%20for%203D%20printing.md)
Motor hub | Set 1 component 1
Tool | # in Table S1
Allen key for M3 | 48

16

### 7. Mount the motor hub on the aluminium profiles

Follow instructions in video 7. Mounting the motor hub on the aluminium profiles. (https://youtu.be/7jGVR2kCcX8)

Component | # in Table S1
The motor hub assembled in step 6 | -
1x T2020 black aluminium profile 40 cm long | 20
2x T2020 black aluminium profile 8 cm long | 20
12x M5 8 mm screws, button head, hex socket, black | 33
12x M5 T-nuts for T2020 aluminium profile | 37
Tool | # in Table S1
Allen key for M5 | 48

17

### 8. Mount bearings on the bearing guides

Follow instructions in video 8. Mounting the bearings. (https://youtu.be/Blg7TRkFgC0)

Component | # in Table S1
3x ball bearings | 22
6x M5 washers | 39
3x M5 hexagonal nuts | 38
3x M5 x 16 mm screws, button head, hex socket, black | 35
Component | # in Table S2 (https://github.com/AlyonaMinina/SPIRO.Hardware/blob/master/Supplementary%20Tables/Table%20S2.%20Structural%20parts%20of%20SPIRO%20for%203D%20printing.md)
3x bearing guides | Set 1 components 2 and 3
Tool | # in Table S1
Allen key for M5 | 48

18

### 9. Mount the positional sensor on the bearing guide

Follow the instructions in video 9. Mounting the mini microswitch. (https://youtu.be/lMoPr70Eqks)

Component | # in Table S1
The mini microswitch soldered in the step 5 | –
2x M2.5 12 mm screws, flat head countersunk, black | 25
2x M2.5 hexagonal nuts | 27
The bearing guide assembled in the step 8 | –
Component | # in Table S2 (https://github.com/AlyonaMinina/SPIRO.Hardware/blob/master/Supplementary%20Tables/Table%20S2.%20Structural%20parts%20of%20SPIRO%20for%203D%20printing.md)
Mini microswitch housing | Set 1 component 4
Tool | # in Table S1
Screwdriver for M2.5 | 47

19

### 10. Mount bearing guides on the aluminium profiles and install the slot cover

Follow instructions in video 10a. Mounting bearing guides (https://youtu.be/xws4S3Z_6DU) and video 10b. Aluminium profile slot cover. (https://youtu.be/Rp3FlnVSsGg)

Component | # in Table S1
Bearing guides assembled in steps 8 and 9 | –
9x M5 8 mm screws, button head, hex socket, black | 33
9x M5 T-nuts for T2020 aluminium profile | 37
2020 Aluminium Profile Slot Cover black, ca 1 m | 21
Tool | # in Table S1
Allen key for M5 | 48

20

### 11. Mount the aluminium rail for the LED frame

Follow instructions in video 11. Mounting aluminium rail for LED. (https://youtu.be/rISrH1DNzCk)

Component | # in Table S1
2x Aluminium profiles T2020, black, 14 cm long | 20
M5 16mm bolt, hex head | 35
6x M5 8 mm screws, buttonhead, black | 33
3x M5 T-nuts | 37
2x M5 slide-in brackets for T2020 aluminium profile | 40
Component | # in Table S2 (https://github.com/AlyonaMinina/SPIRO.Hardware/blob/master/Supplementary%20Tables/Table%20S2.%20Structural%20parts%20of%20SPIRO%20for%203D%20printing.md)
Holder for the LED frame rail | Set 1 component 7
1x bottom for a thumb screw | Set 1 component 8
1x cap for a thumb screw | Set 1 component 9
Tool | # in Table S1
Allen key for M5 | 48

Optional: it is advisable to use slots cover on the bottom slot of the profile to enhance stability of the frame.

21

### 12. Mount the LED frame

Follow instructions in video 12. Assembling of the LED illumination: (https://youtu.be/StVlKRspxJU)

- Attach the LED strip to the LED frame.
- Mount the frame to the aluminium rail.
Component | # in Table S1
LED strip assembled in step 4b | –
4x M5 12 mm screws, flat head countersunk | 32
4x M5 T-nuts | 37
Super glue | 50
Component | # in Table S2 (https://github.com/AlyonaMinina/SPIRO.Hardware/blob/master/Supplementary%20Tables/Table%20S2.%20Structural%20parts%20of%20SPIRO%20for%203D%20printing.md)
LED frame, right half | Set 7
LED frame, left half | Set 8
Diffusor, left part (L) | Set 9 component 1
Diffusor, bottom left part (BL) | Set 9 component 2
Diffusor, bottom right part (BR) | Set 9 component 3
Diffusor, top part (T) | Set 10
Diffusor, right part (R) | Set 11
Tool | # in Table S1
M5 Allen key | 48

22

### 13. Mount the vertical rail

Follow instructions in video 13. Mounting the vertical rail (https://youtu.be/AergWlDSAlk)

Component | # in Table S1
2x Aluminium profiles T2020, black, 30 cm long | 20
1x M5 16mm bolt, hex head | 35
1x M5 8 mm screw, button head, hex socket, black | 33
1x M5 slide-in bracket for T2020 aluminium profile | 40
Component | # in Table S2 (https://github.com/AlyonaMinina/SPIRO.Hardware/blob/master/Supplementary%20Tables/Table%20S2.%20Structural%20parts%20of%20SPIRO%20for%203D%20printing.md)
Holder for vertical rail | Set 1 component 6
1x bottom for a thumb screw | Set 1 component 8
1x cap for a thumb screw | Set 1 component 9
Tool | # in Table S1
M5 Allen key | 48

23

### 14. Mount the light screen

Follow instructions in video 14. Mounting the light screen. (https://youtu.be/-hJM8Q_g3cI)

Component | # in Table S1
5x M5 11 mm screws, button head, hex socket, black | 41
5x M5 T-nuts | 37
Component | # in Table S2 (https://github.com/AlyonaMinina/SPIRO.Hardware/blob/master/Supplementary%20Tables/Table%20S2.%20Structural%20parts%20of%20SPIRO%20for%203D%20printing.md)
Left part of the light screen | Set 6
Right part of the light screen | Set 5
Tool | # in Table S1
M5 Allen key | 48

24

### 15. Assemble and mount the Borg's nest

Follow instructions in the video 15. Assembling and mounting of the Borgs nest. (https://youtu.be/5mJFkdKQDbM) The pinout scheme for all components is available in Fig. 1B. Additionally, connections for individual components are illustrated in Figs. 2, 4 and 6.
We recommend to prepare the microSD card according to the instructions in step 18 of this manual and to insert it into the Raspberry Pi before assembly.
Component | # in Table S1
1x Raspberry Pi 3B+ | 1
Motor driver + SparkFun power control kit + DC connector wired in
steps 3 and 4
| –
2x M2.5 12 mm screws, flat head countersunk | 25
2x M2.5 12 mm screws, button head | 24
4x M2.5 hex nuts | 27
4x M3 12 mm screws, button head | 28
4x M3 20 mm screws, flat head countersunk | 29
8x M3 hex nuts | 30
1x M5 11 mm screw, button head, black | 41
2x M5 T-nuts | 37
Component | # in Table S2 (https://github.com/AlyonaMinina/SPIRO.Hardware/blob/master/Supplementary%20Tables/Table%20S2.%20Structural%20parts%20of%20SPIRO%20for%203D%20printing.md)
1x Borgs nest | Set 2 component 1
1x Lid for the Borg's nest | Set 2 component 2
1x DC connector lid | Set 2 component 3
1x SparkFun holder | Set 2 component 4
Tool | # in Table S1
M2.5 screwdriver | 47
M3 and M5 Allen keys | 48
Tweezers | -

25

### 16. Mount and connect the camera

Here we provide instructions for two configurations of SPIRO that differ solely in the focusing solutions for the camera: (i) manual focus; (ii) motorized focus.

The motorized focus configuration requires a camera assembled from a Raspberry Pi v2 camera, in which the original camera module is replaced by the Arducam camera IMX219 8 MP Auto Focus camera module (Table S1). The solution with manual focusing requires unmodified Raspberry Pi v2 camera only (Table S1).

Both configurations provide the same quality of images. The motorized focus configuration is approximately 25 Euros more expensive than the configuration with the manual focus adjustment. However, the motorized option allows focus adjustment remotely from SPIRO software and thus enables considerably more convenient operation of the robot.

26

16a. For the configuration with manual focus (alternative to 16b)

Follow instructions in the video 16. Mounting and connecting the camera. (https://youtu.be/1_wpKMmS_WY)

Component | # in Table S1
1x Raspberry Pi V2 Camera | 18a
1x Flex cable, ca 25 cm long | 17
4x M2.5 8mm screws, flat head countersunk | 26
4x M2.5 hex nuts | 27
2x M5 16mm bolts, hex head | 35
2x M5 T-nuts | 37
Component | # in Table S2 (https://github.com/AlyonaMinina/SPIRO.Hardware/blob/master/Supplementary%20Tables/Table%20S2.%20Structural%20parts%20of%20SPIRO%20for%203D%20printing.md)
1x Housing for Pi camera | Set 3b component 1
1x Lid for camera housing | Set 3b component 2
2x Bottom for a thumb screw | Set 3b component 3
2x Cap for a thumb screw | Set 3b component 4
1x Stabilizer for the camera | Set 3b component 5
Tool | # in Table S1
M2.5 screwdriver | 47
M3 Allen key | 48

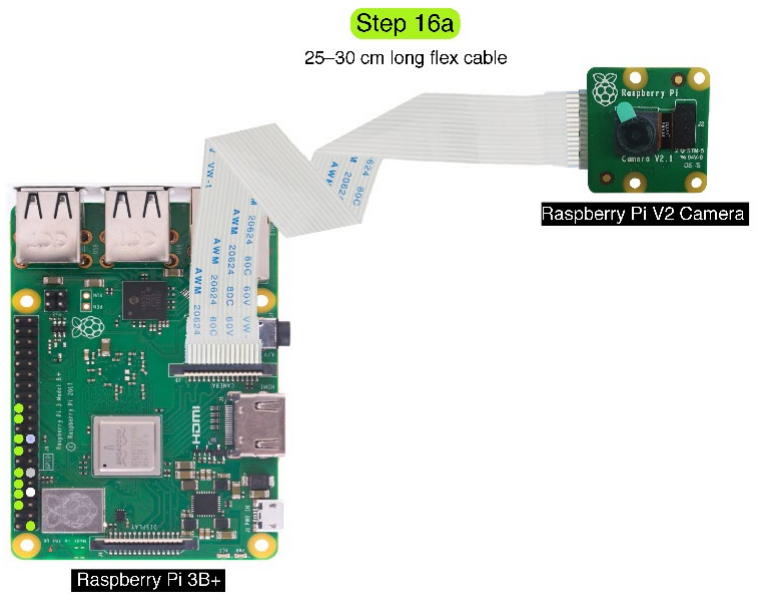
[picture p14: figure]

Figure 7. Connecting the Raspberry
| Pi camera v2 with manual focus The Raspberry Pi V2 camera is con- nected to the camera port on the Rasp- berry Pi computer via a white flex cable. Please note that the metal surfaces on the flex cable should be facing the metal pins in the ports on the Raspberry Pi computer and on the camera PCB.

27

16b. For the configuration with motorized focus (alternative to 16a)
- Replace the original module of the Raspberry Pi V2 camera with the Arducam module. Please follow the instructions provided by Arducam⁴. (https://youtu.be/Zy1FYLadOfA)
- Connect the camera board to the Raspberry Pi computer. The procedure is the same as for the 16a step shown in the video 16. Mounting and connecting the camera. (https://youtu.be/1_wpKMmS_WY)
- Optionally, it is possible to also use printed washers placed on the thumb screws between the camera house and the aluminium profile. They increase the space left for the flex cable and thus reduce mechanical stress on it when the camera is moved along the vertical axis.
Figure 8. Connecting the camera with the Arducam motorized camera module. Firstly, the original Raspberry Pi V2 camera module is replaced by the Arducam module. Secondly, the Raspberry Pi V2 camera board is connected to the camera port on the Raspberry Pi computer via a white flex cable. Please note that the metal surfaces on the flex cable should be facing the metal pins in the ports on the Raspberry Pi computer and on the camera PCB.

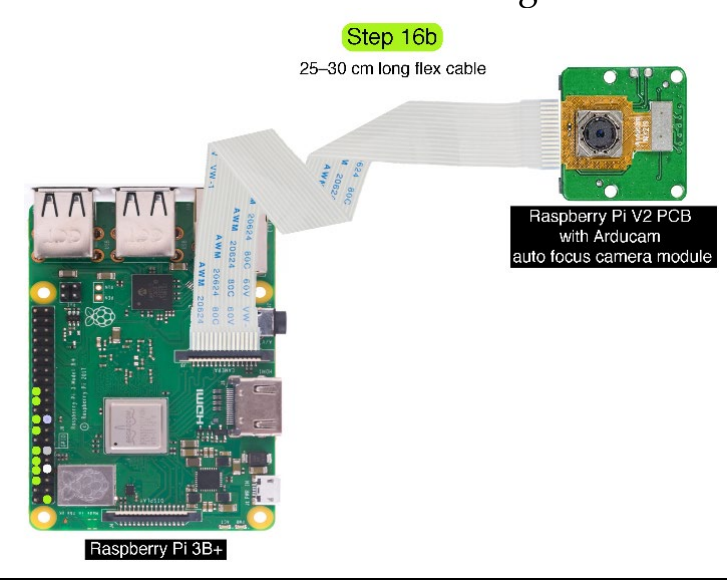
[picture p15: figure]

Component | # in Table S1
1x Raspberry Pi V2 Camera | 18b
1x Arducam IMX219 8MP Auto Focus Camera Module | 18b
1x Flex cable, ca 25 cm long | 17
4x M2.5 8mm screws, flat head countersunk | 26
4x M2.5 hex nuts | 27
2x M5 16mm bolts, hex head | 35
2x M5 T-nuts | 37
Component | # in Table S2 (https://github.com/AlyonaMinina/SPIRO.Hardware/blob/master/Supplementary%20Tables/Table%20S2.%20Structural%20parts%20of%20SPIRO%20for%203D%20printing.md)
1x Housing for Arducam camera module | Set 3a component 1
1x Lid for camera housing | Set 3a component 2
2x Cap for a thumb screw | Set 3a component 3
2x Bottom for a thumb screw | Set 3a component 4
2x washers | Set 3a component 5
Tool | # in Table S1
M2.5 screwdriver or allen key | 47

28

### 17. Assemble and mount the stage

Follow instructions in video 17. Assembling and mounting of the cube. (https://youtu.be/C9aMrJE2Ksw) While mounting the shaft coupling, make sure that more than half of it is covering the motor shaft. It is of utmost importance to fix the screws on the coupling as tightly as possible to prevent unwanted wobbling during the stage rotation.

It is possible to prevent the vibrations of the stepper motor from resonating inside the cube. For this, prepare a washer made out of Parafilm (four layers of 2x2cm Parafilm squares suffices) to be fitted between the hex head of the M5 bolt and the cube bottom. It is crucial to ensure that the hex head of M5 is completely sunken into the well designed for it (not shown in the video).

Optionally, the bolt can be additionally secured in its position with a washer and a screw nut (M5) fastened under the cube.

Component | # in Table S1
1x Rigid shaft coupling M5 to M5 | 23
2x M2.5 8mm screws, flat head countersunk | 26
2x M2.5 hex nuts | 27
1x M5 20 mm bolt, hex head | 36
Component | # in Table S2 (https://github.com/AlyonaMinina/SPIRO.Hardware/blob/master/Supplementary%20Tables/Table%20S2.%20Structural%20parts%20of%20SPIRO%20for%203D%20printing.md)
1x Cube | Set 4
1x Mini microswitch pin (tiny dick) | Set 1 component 5
Tool | # in Table S1
M2.5 screwdriver | 47

29

## SPIRO assembly is complete!

30

### 18. Software installation

SPIRO software should be installed on a formatted microSD card that is then placed into a slot on the Raspeberry Pi board (Fig. 9). For installation, please follow the instructions provided in the SPIRO Software Repository⁵. (https://github.com/jonasoh/spiro#installation) The acquired data will be stored on the same card, thus the capacity of the microSD card will determine how many images you can store. As a rule of thumb, one image will take up 8 MB. A 64 GB card costs around €10 at the time of writing this manual and can hold approximately 8000 images. Choose a well-known brand, as these cards are more reliable. Cards rated A, e.g. A1, are the best choice for performance.

Please note, that for completing the installation you will need to temporarily connect a keyboard to the USB port (Fig. 9A) and a monitor to the HDMI port (Fig. 9) of the Raspberry Pi computer.
Installing from the Supplementary File

This step is only needed if the software repository is not accessible! In case the SPIRO Software Repository is not available, installation from the provided Supplementary File is possible. This file also contains the installation instructions in the file README.md. In this case, the supplementary file must be transferred to the Raspberry Pi. This is most easily accomplished using an SFTP client, such as MobaXterm (Windows only) or FileZilla (Windows/Linux/Mac). After transferring the zip file (spiro-software.zip), enter the following command to install the SPIRO software and its dependencies:
sudo pip3 install spiro-software.zip
This command replaces the corresponding command stated in the online installation instructions (starting with sudo pip3 install).

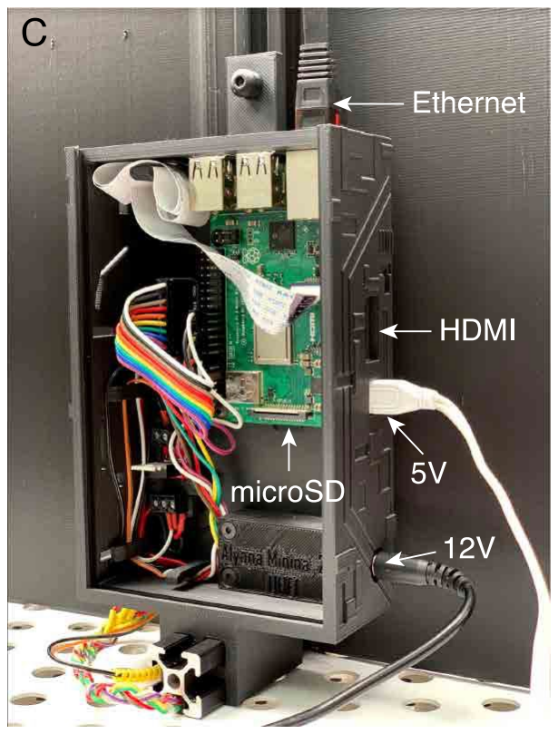
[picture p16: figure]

31

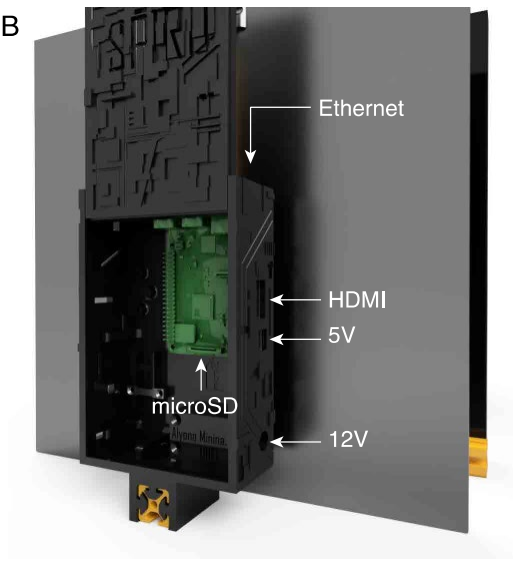
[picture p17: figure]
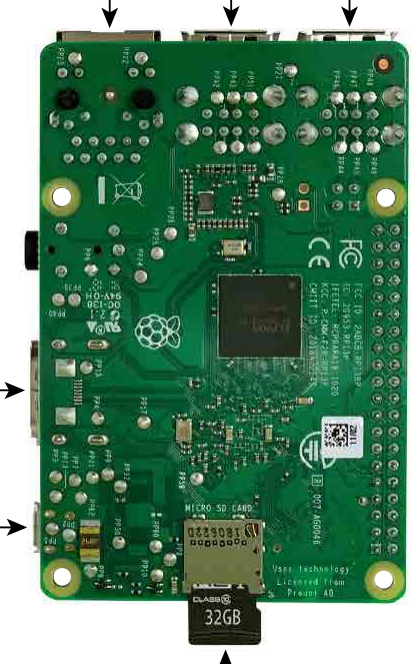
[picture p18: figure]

Figure 9. Connecting power and network cables and placing the microSD card
(A) Bottom view of the Raspberry Pi 3B+ with indicated slot for microSD card and ports for Ethernet, power and HDMI cables. (B) Rendering of assembled SPIRO showing placement of microSD card and ports for connecting power, Ethernet and HDMI cables. (C) Photo of assembled SPIRO showing the components indicated on (A) and (B).
Component | # in Table S1
1x microSD card | 12
1x Ethernet cable | 51

Tool
A computer with microSD card reader
A monitor with an HDMI cable
USB keyboard
Internet access, either via WiFi or ethernet

32

### 19. Network setup

The SPIRO software is primarily controlled over the network using a web interface. Three basic modes of network connectivity are possible:

1. connecting to an existing network via an Ethernet cable
2. connecting to an existing network via Wi-Fi
3. acting as a Wi-Fi hotspot without connecting to an existing network.

The choice of network connection mode depends on the local network settings, such as firewall or other network policies and availability of network connections in the facility where SPIRO is physically deployed.

Connection modes 1 and 2 are the most flexible, in that they allow for online updating of the software and for remotely interacting with the software. However, local network policies may not allow for the use of these modes. For accessing the SPIRO software, TCP ports 22 and 8080 need to be reachable from the client. Check with your network administrator whether this is the case.

Please note, that by default the Raspberry Pi computer will be assigned a dynamic IP address. This means that every time the robot is disconnected and reconnected to the network, the address may change and you would need to physically plug a screen and keyboard into the SPIRO HDMI and USB ports to find out its current address. Therefore, we strongly recommend to request a static IP (or a dynamic hostname) for your SPIRO from your local network administrator.

Connection mode 3, hotspot mode, allows for interacting with the system without a accessing an existing network. Instead, the user connects to the Wi-Fi network named SPIRO-XXXXXX (where XXXXXX is a pseudorandom identifier). After connecting to this Wi-Fi network, the SPIRO system can be found at the convenience address spiro.local (i.e., the web interface may be reached at http://spiro.local:8080). The Wi-Fi hotspot does not route any traffic, and thus does not provide access to any other internet resources.

Wi-Fi hotspot mode can be enabled at the same time as the system is connected to an existing network. This option may be desirable if there is a network connection available, but firewall policies restrict access to the system. In this case, the network connection can be used for system updates, whereas the hotspot connection is used for interacting with the software. Hotspot mode is enabled by following the instruction in the online installation instructions. (https://github.com/jonasoh/spiro#enabling-the-wi-fi-hotspot)

33

### Links

1. https://www.youtube.com/watch?v=Qps9woUGkvI&ab_channel=oneTesla.
2. https://github.com/AlyonaMinina/SPIRO.Hardware.
3. https://www.prusa3d.com/prusaslicer/.
4. https://youtu.be/Zy1FYLadOfA.
5. https://github.com/jonasoh/spiro.

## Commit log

2019-05-19 files arrangment
    [Structural parts set 3b. Alyona Minina. 2019. UHEI.stl]
2019-05-19 strutctural parts for SPIRO
    [3b. Structural parts set 3b. Alyona Minina. 2019. UHEI.stl, 4. Structural parts set 4. Alyona Minina. 2019. UHEI.stl, 5. Structural parts set 5. Alyona Minina.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]
2019-05-19 Structural parts for PSIRO
    [Structural parts set 3b. Alyona Minina. 2019. UHEI.stl, Structural parts set 4. Alyona Minina. 2019. UHEI.stl, Structural parts set 5. Alyona Minina. 2019. UHE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]
2019-05-19 SPIRO. Structural parts for 3D printing
    [Structural parts for 3D printing set 3b. Alyona Minina. 2019. UHEI.stl, Structural parts for 3D printing set 4. Alyona Minina. 2019. UHEI.stl, Structural parts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]
2019-09-01 updated hardware files
    [Set 10. Alyona Minina. 2019. UHEI.stl, Set 11. Alyona Minina. 2019. UHEI.stl, Set 13. Alyona Minina. 2019. UHEI.stl, Set 2. Alyona Minina. 2019. UHEI.stl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]
2019-09-01 Updated screenshots from slic3r
    [Set 02. Alyona Minina. 2019. UHEI.stl, Set 03a. Alyona Minina. 2019. UHEI.stl, Set 03b. Alyona Minina. 2019. UHEI.stl, Set 04. Alyona Minina. 2019. UHEI.stl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]
2019-09-01 Create Table S2. Structural parts of SPIRO for 3D printing.pdf
2019-09-02 figures for the assembly manual
2019-09-02 Create SPIRO assembly instructions v3 for github.pdf
2019-09-02 Hardware assembly manual v3
2019-09-02 assembly manual v3
2019-09-06 Create set 14. optional. Alyona Minina. 2019. UHEI.stl
    [set 14. optional. Alyona Minina. 2019. UHEI.stl]
2019-09-26 add quick printing reference
2019-09-26 add link to the printing reference sheet
2019-09-26 make the print sheet link more prominent
2019-11-19 make printing ref links point directly to stls
2020-03-02 borgs nest update
    [Set 02. Alyona Minina. 2019. UHEI.stl, Set 2. Alyona Minina. 2019. UHEI.stl]
2020-03-11 Rename printing-reference.md to Table S2. Structural parts of SPIRO for 3D printing
2020-03-11 Revert "Rename printing-reference.md to Table S2. Structural parts of SPIRO for 3D printing"
    This reverts commit 91e2eae07965c939cc58fb3faeaca94900443ed3.
2020-03-11 Rename printing-reference.md to Table S2. Structural parts of SPIRO for 3D printing.md
2020-03-25 Update Table S2. Structural parts of SPIRO for 3D printing.md
2020-03-25 new links to rep figures
    [Set 03a. Alyona Minina. 2019. UHEI.stl, Set 03b. Alyona Minina. 2019. UHEI.stl, Set 04. Alyona Minina. 2019. UHEI.stl, Set 05. Alyona Minina. 2019. UHEI.stl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]
2020-04-02 upgraded design for the tiny dick mount
    [Set 02. Alyona Minina. 2019. UHEI.stl, Set 04. Alyona Minina. 2019. UHEI.stl, Set 13. Alyona Minina. 2019. UHEI.stl, Set 2. Alyona Minina. 2019. UHEI.stl]
2020-04-02 Revert "upgraded design for the tiny dick mount"
    This reverts commit b1dc112221c2d3c68108b8bbe935f475ce284bfa.
    [Set 02. Alyona Minina. 2019. UHEI.stl, Set 04. Alyona Minina. 2019. UHEI.stl, Set 13. Alyona Minina. 2019. UHEI.stl, Set 2. Alyona Minina. 2019. UHEI.stl]
2020-04-02 Update of the tiny dick mount
    [Set 02. Alyona Minina. 2019. UHEI.stl, Set 04. Alyona Minina. 2020. UHEI.stl]
2020-04-02 removing duplicate files
    [Set 13. Alyona Minina. 2019. UHEI.stl]
2021-03-04 Updates of 3D model files
    [SPIRO seed plating guide for 12cm square plates.stl, SPIRO seed plating guide for 9 cm round plates.3mf, SPIRO seed plating guide for 9 cm round plates.stl, Se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]
2021-03-04 Create SPIRO seed plating guide for 12 cm square plates.3mf
    [SPIRO seed plating guide for 12 cm square plates.3mf]
2021-03-09 update of the assembly instructions.pdf
2021-03-10 Assembly instructions update
2021-05-18 set 1 upgrade 1
    -motor hub v2 with smoothened corners (less plastic to print)
    -new bearing guide + housing for mounting the microswitch to stabilize it if the screws get lose
    [Set 01. Alyona Minina. 2019. UHEI.3mf, Set 01. Alyona Minina. 2019. UHEI.stl]
2021-05-18 Update Table S2. Structural parts of SPIRO for 3D printing.md
    set 01. upgrade 2021.05.18
2021-05-20 Upgrades of set 2 and 4
    [Set 01 for 2 SPIRO systems.3mf, Set 02. Alyona Minina. 2019. UHEI.3mf, Set 02. Alyona Minina. 2019. UHEI.f3d, Set 02. Alyona Minina. 2019. UHEI.stl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]
2021-10-26 Hardware updates from July 2021 set 1 and 2
    [Set 01 Component 1 Motor hub (v3).stl, Set 01 Component 2 Bearings guide (v10).stl, Set 01 Component 3 Bearing guide with the mounting for microscwitch (v6).st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]
2021-10-26 SPIRO hardware updates from July 2021. sets 3-11
    [Set 01 Component 5 Tiny dick (v6).stl, Set 03 Component 1 Arducam module camera house (v6).stl, Set 03 Component 2 Arducam module camera house lid (v6).stl, Se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]
2021-11-02 new version of the Borgs nest to accommodate Raspberry pi 4
    [Set 02 Component 1 Borgs nest (v2 for RPi 3).stl, Set 02 Component 1 Borgs nest (v4 for RPi 4).stl]
